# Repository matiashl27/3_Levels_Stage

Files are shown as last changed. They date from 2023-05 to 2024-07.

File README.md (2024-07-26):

# Strobe-enhanced microscopy stage for microfluidic droplet generation 

The strobe-enhanced microscopy stage is a free and open-source workstation for imaging fast processes, particularly developed for microfluidic droplet generation. It uses the lens from the Raspberry Pi Camera to produce a microscope with a field of view of almost 1mm and a strobe illumination based on a high-power LED for imaging fast-moving objects. Custom electronics allow the synchronization between the LED and the camera to capture sharp images of fast-moving droplets and other objects.

> **Note:** Most parts of this stage are original designs, and some items were modified from the open-source hardware [OpenFlexure flat-top microscope](https://rwb27.gitlab.io/openflexure-flat-top-microscope/), this includes some elements on this page and in the assembly instructions.

Find about more about this platform and other open-source hardware for bioimaging on the [LIBRE hub website](https://librehub.github.io/). Follow us! [#twitter](https://twitter.com/WenzelLab) [#YouTube](https://www.youtube.com/@librehub) [#LinkedIn](https://www.linkedin.com/company/92802424) [#instagram](https://www.instagram.com/wenzellab/) [#Printables](https://www.printables.com/@WenzelLab), [IIBM website](https://ingenieriabiologicaymedica.uc.cl/en/people/faculty/821-tobias-wenzel)

<!--- ## Table of Contents --->

<!--- ## Background --->

## Usage

### Instructions

* [Assembly instructions](https://wenzel-lab.github.io/strobe-enhanced-microscopy-stage/)
    * [Parts list](https://wenzel-lab.github.io/strobe-enhanced-microscopy-stage/3-level-station_BOM.html)
    * [Software installation](https://wenzel-lab.github.io/strobe-enhanced-microscopy-stage/software-installation.html)
* Usage instructions
	* [Software usage](https://wenzel-lab.github.io/strobe-enhanced-microscopy-stage/usage.html)

This project is documented with GitBuilding - an OpenSource project for documenting hardware projects. For more information on the GitBuilding project, or how
to install GitBuilding please see the [GitBuilding website](http://gitbuilding.io)

## Design files and source code

* Hardware designs
    * [Microscope hardware and assembly instructions (source)](https://github.com/wenzel-lab/strobe-enhanced-microscopy-stage)
    * [Pi Hat](https://github.com/wenzel-lab/moldular-microfluidics-workstation-controller/tree/master/module-pi/pi_pcb)
    * [Strobe module](https://github.com/wenzel-lab/moldular-microfluidics-workstation-controller/tree/master/module-fast-imaging)
* Software source code
    * [Microscope server](https://github.com/wenzel-lab/moldular-microfluidics-workstation-controller/blob/master/module-pi/webapp.zip) (This code runs on the built-in Raspberry Pi and includes the web application for the user interface.)
    * Microscope operating system (This collates all software and builds a pre-written SD card image for the Raspberry Pi.) - Coming soon
 
### How do I edit the documentation?

To edit the documentation you do not need to install anything, but you will need to
install something to build the final version of the documentation (such as a website).
The documentation files can be opened in a plain text editor such as Windows Notepad,
Notepad++, gedit, VS Code, etc. GitBuilding also comes with a browser-based editor that
displays has a live display of the final HTML documentation.

If you have ever used [markdown](https://www.markdownguide.org/basic-syntax/) you will
notice that the files you are editing are markdown files. GitBuilding uses an extended
markdown syntax (that we call BuildUp). This allows you to keep track of parts in the
documentation. More detail on the documentation is available on the
[GitBuilding website](https://gitbuilding.io/syntax/). There is also additional
[syntax for configuration](https://gitbuilding.io/syntax/buildconfsyntax), and for
[part libraries](https://gitbuilding.io/syntax/builduplibrary/).

## Contribute

You're free to fork the project and enhance it. If you have any suggestions to improve it or add any additional functions make a pull-request or [open an issue](https://github.com/wenzel-lab/strobe-enhanced-microscopy-stage/issues/new).
For interactions in our team and with the community applies the [GOSH Code of Conduct](https://openhardware.science/gosh-2017/gosh-code-of-conduct/).

## License

[CERN OHL 2W](LICENSE) © Pierre Padilla-Huamantinco, Matías Hurtado, and Tobias Wenzel. This project is Open Source Hardware - please acknowledge us when using the hardware or sharing modifications.

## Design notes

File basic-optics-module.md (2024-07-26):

# Assemble the basic optics module

{{BOM}}

[M3 nut]: parts/mech/nuts.md "{cat:mechanic}"
[M2x5mm cap head screw]: parts/mech/M2-5.md "{cat:mechanic}"
[M3x10mm cap head screw]: parts/mech/M3-10.md "{cat:mechanic}"
[Raspberry Pi Camera Module v2]: parts/elect/rpi-camera-v2.md "{cat:electronic}"
[Pi camera ribbon cable]: parts/elect/rpi-camera-ribbon-cable.md "{cat:electronic}"
[1.5mm Ball-end Allen key]: parts/tools/1.5mmBallEndAllenKey.md "{cat:tool}"
[Pi Camera lens tool]: parts/tools/pi_camera_lens_tool.md "{cat:tool, note: 'This should come with the Raspberry Pi Camera Module. If it is missing, you can 3D print a workaround lens remover.'}"
[Lens spacer]: models/lens-spacer.stl "{previewpage}"
[Pi Camera platform]: models/camera-platform.stl "{previewpage}"
[Nitrile gloves]: parts/consumables/gloves.md "{cat:consumable}"

The imaging optics for this workstation version consist of the Raspberry Pi camera and the lens from the camera. To create a microscope, the lens is separated from the camera. This makes quite a good microscope objective with a field of view about 950μm across.

## Visually inspect the lens spacer {pagestep}

Take the [lens spacer][Lens spacer](fromstep){qty:1, cat:printedpart} and confirm that:

* It has been printed in black.
* It is dust free (You can blow air through to clean it)
* The central shaft is not obstructed by strings of plastic.

## Remove Pi Camera Lens {pagestep}

>! **Caution!** The camera board is static sensitive. Before touching the Pi Camera, touch a metal-earthed object. If you own one, consider wearing an anti-static strap.

* Use [nitrile gloves][Nitrile gloves]{Qty:2} to manipulate camera and lens. 
* Take the [Pi Camera][Raspberry Pi Camera Module v2]{qty:1} out of the package. Make sure to **hold it only by the sides of the board**.
* Take the protective film off the lens.
* Take the [Pi Camera lens tool]{qty: 1} and place it over the lens
* Slowly unscrew the lens (About 4 full turns of the tool)
* Carefully lift off the lens.
* Save the lens and the camera.

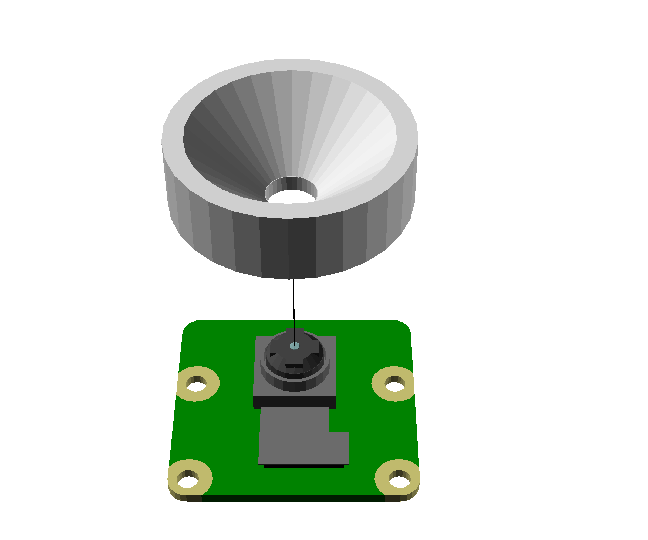
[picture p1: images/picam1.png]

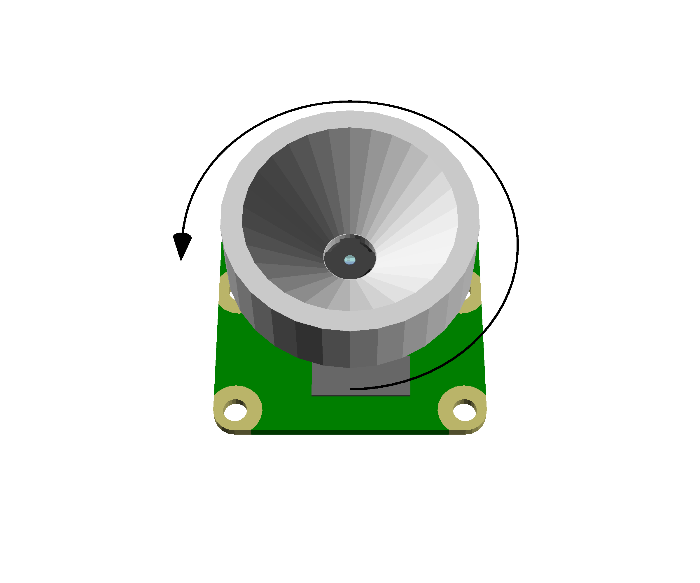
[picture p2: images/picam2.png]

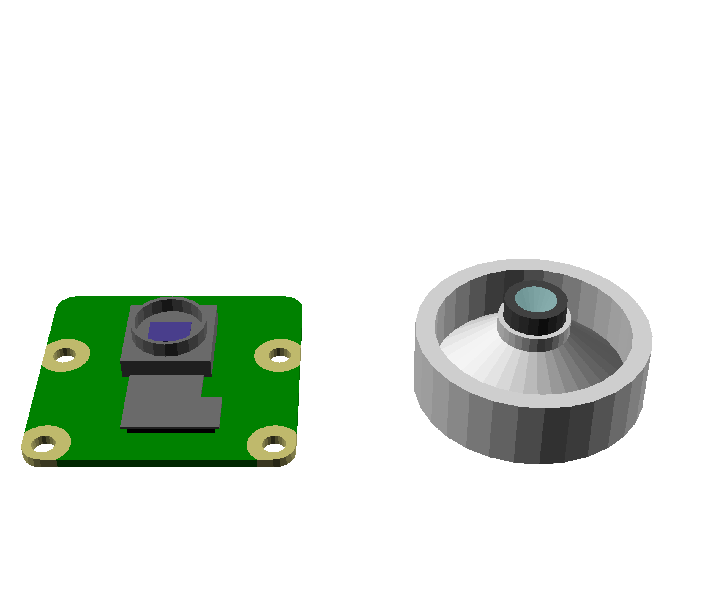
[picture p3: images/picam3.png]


## Push-fit the lens {pagestep}

* Place the Pi Camera lens on a clean surface with the side opposite the camera sensor on the bottom.
* Push the lens spacer down onto the lens until it clicks into place.

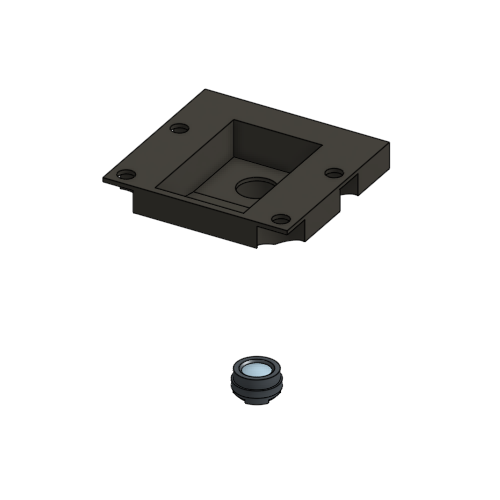
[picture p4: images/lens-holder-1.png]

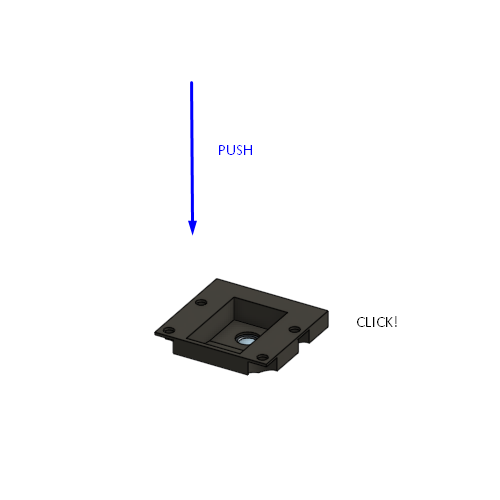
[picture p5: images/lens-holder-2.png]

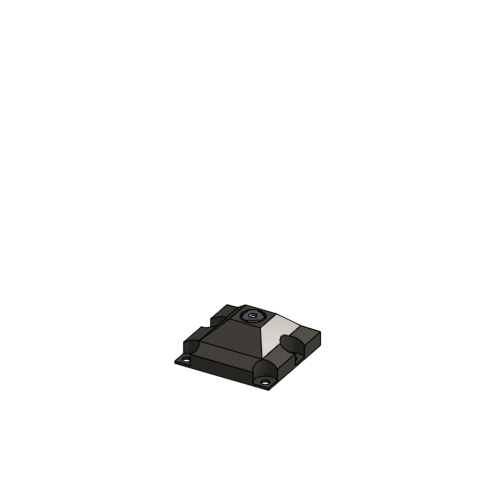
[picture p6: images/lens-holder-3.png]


## Attach the Pi Camera {pagestep}

* Take the Pi Camera and place it on top of the [pi camera platform][Pi Camera platform](fromstep){qty:1, cat:printedpart}.
* Place the lens spacer over the camera.
* Use four [M2x5mm cap head screws][M2x5mm cap head screw]{qty:4} to secure the three parts together using a [1.5mm Ball-end Allen key]{qty:1}

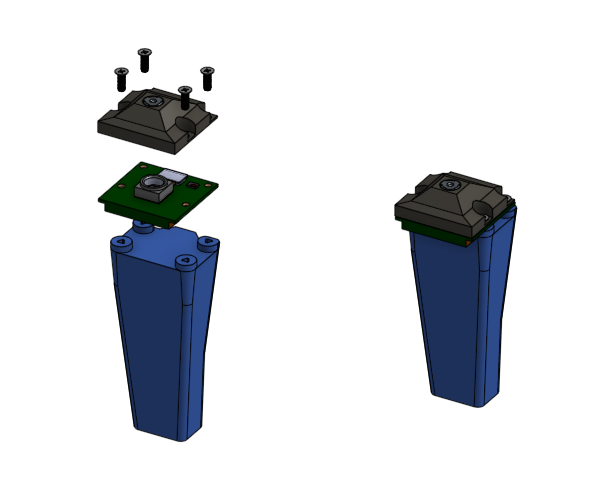
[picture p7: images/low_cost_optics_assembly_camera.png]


## Attach the mounting screw {pagestep}

* Take an [M3 nut]{qty:1} and push it into the nut trap from the top
* Take an [M3x10mm cap head screw]{qty: 1} and screw it into the nut.
* Only screw it in a couple of turns. About 5 mm of thread should still be visible.

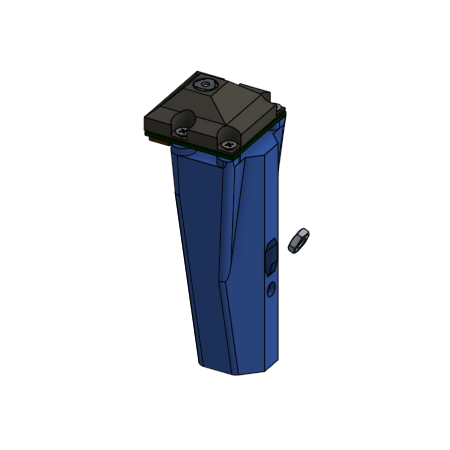
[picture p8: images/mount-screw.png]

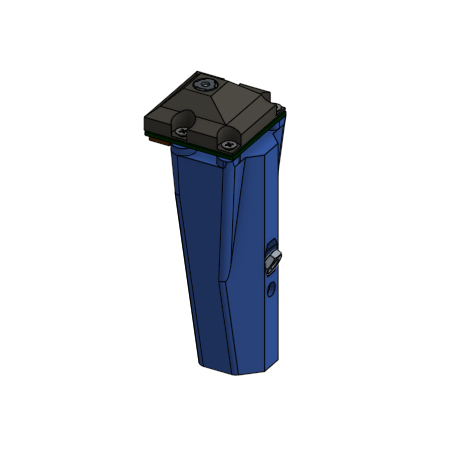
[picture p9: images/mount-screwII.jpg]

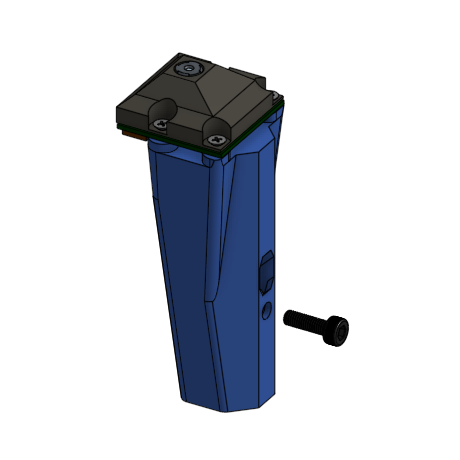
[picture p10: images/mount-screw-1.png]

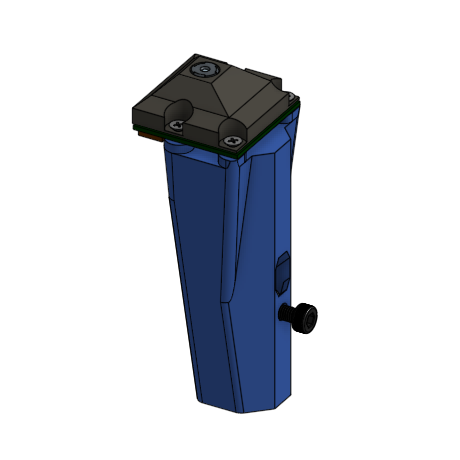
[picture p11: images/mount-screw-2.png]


## Connect ribbon cable {pagestep}

* Take the [Pi Camera ribbon cable][Pi camera ribbon cable]{qty:1}
* Pull the catch forward on the exposed Pi Camera connector
* Insert the ribbon cable with the contacts towards the board
* Close the catch on the connector

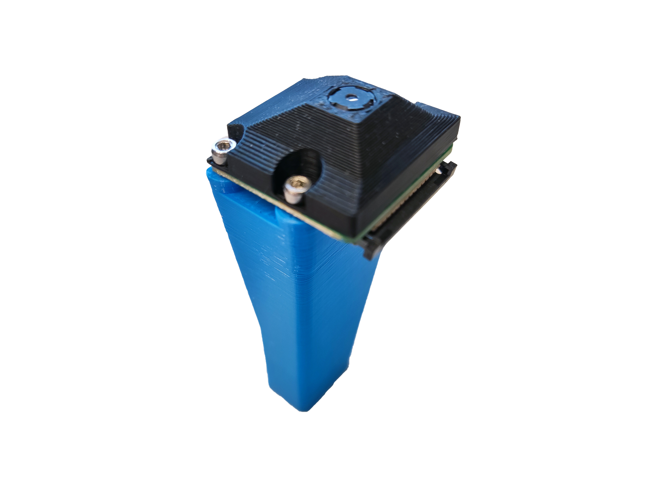
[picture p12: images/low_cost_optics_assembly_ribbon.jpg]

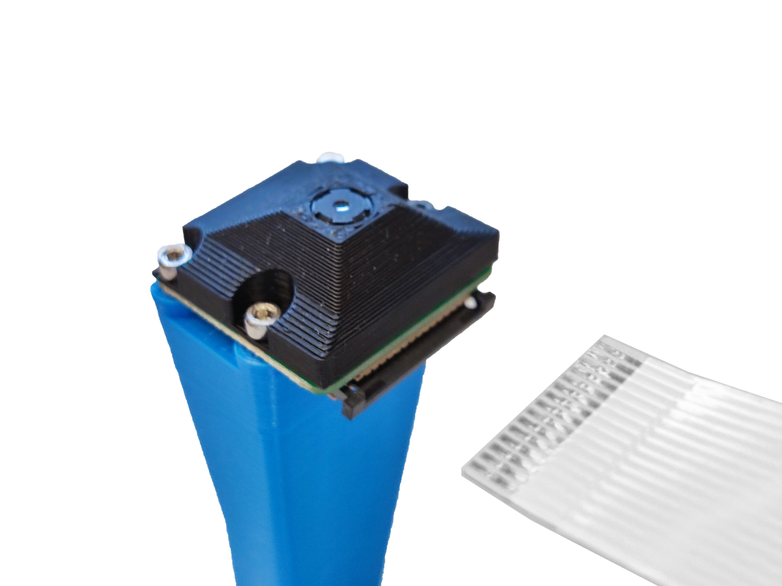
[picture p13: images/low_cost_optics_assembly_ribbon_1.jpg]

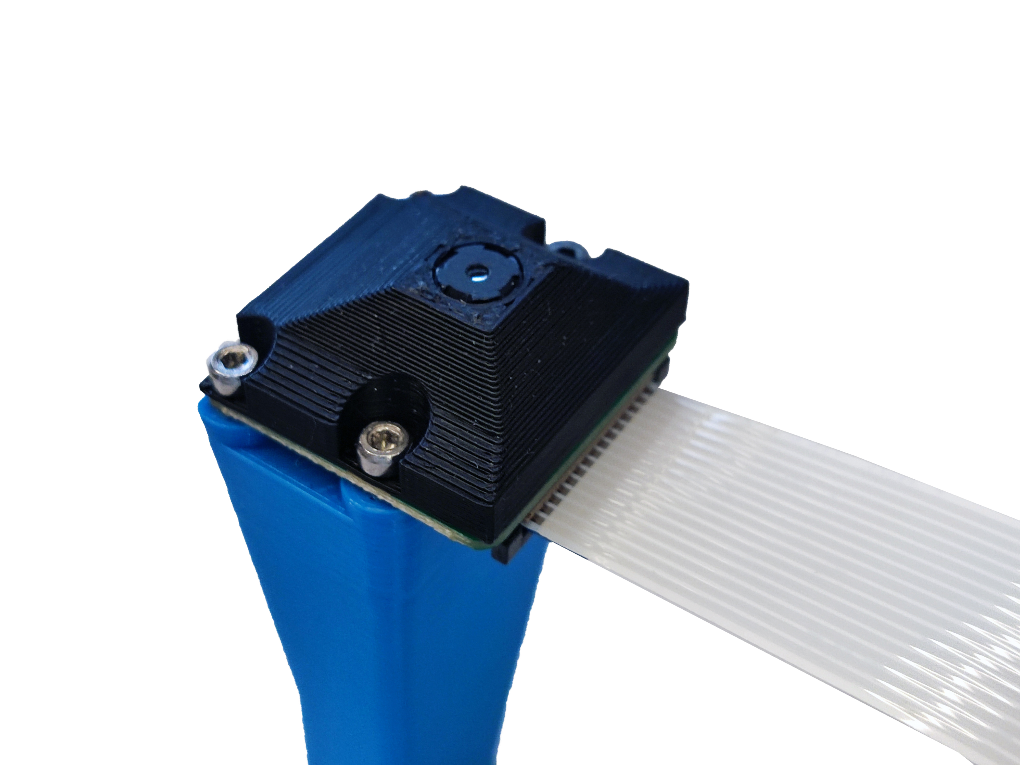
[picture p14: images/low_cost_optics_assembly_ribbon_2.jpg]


## Set the complete module aside {pagestep}

Set the [complete optics module]{output, qty:1} aside in a safe place.

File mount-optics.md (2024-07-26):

# Mount the optics

{{BOM}}

[2.5mm Ball-end Allen key]: parts/tools/2.5mmBallEndAllenKey.md "{cat:tool}"

## Mount the optics assembly {pagestep}

* Get the [2.5mm Ball-end Allen key]{qty:1} ready
* Take the [complete optics module](fromstep){qty:1, cat:subassembly} and pass it between the top and middle plates of the [main structure](fromstep){qty:1, cat:subassembly}.
* Insert the exposed mounting screw on the optics module through the keyhole on the z-actuator.

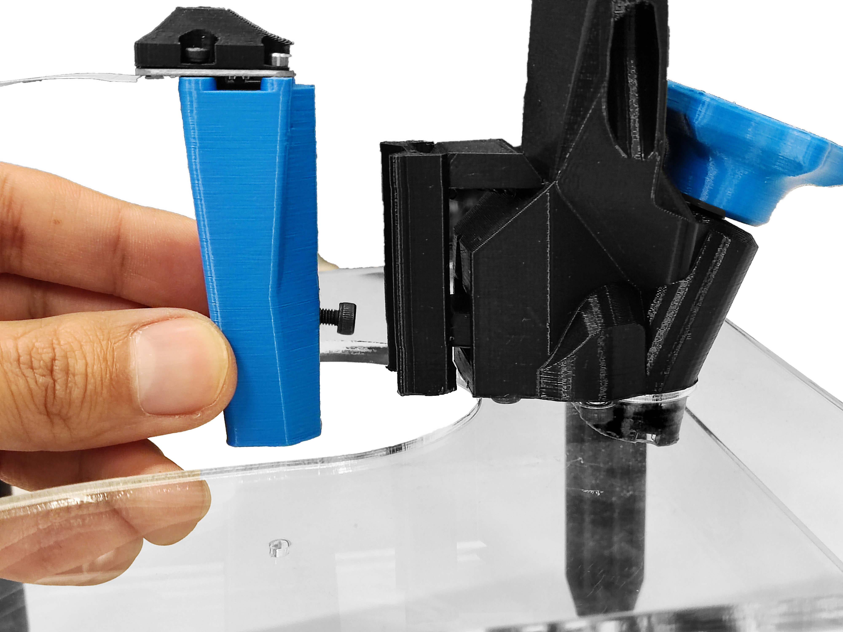
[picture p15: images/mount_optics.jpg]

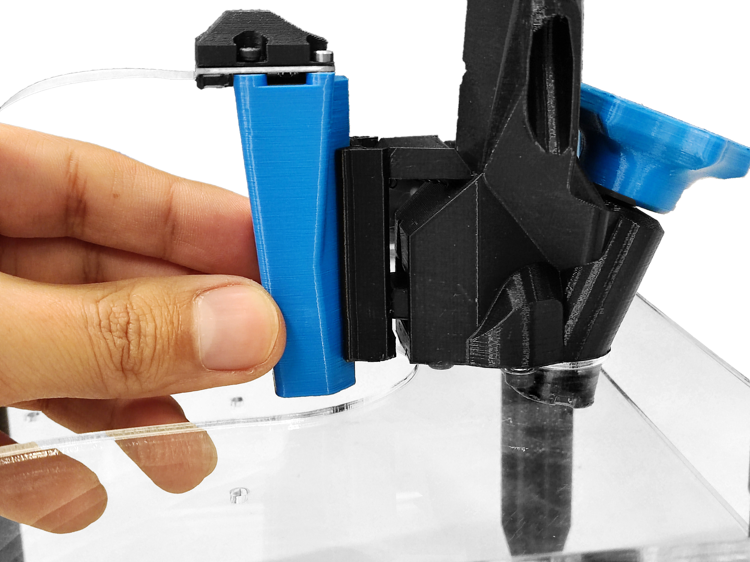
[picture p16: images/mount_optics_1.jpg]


## Adjust the optics assembly {pagestep}

* Insert the Allen key through the teardrop-shaped hole on the front of the z-actuator until it engages with the mounting screw.
* Slide the optics module up the keyhole.
* Tighten the screw with the Allen key to lock the optics.
* The optics module position can be changed later using the thumbwheel or mounting screw for different applications. 



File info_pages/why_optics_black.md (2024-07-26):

# Why print the optics module or lens spacer in black?

The optics module or lens spacer is used to separate the imaging optics from the camera sensor. In an ideal microscope the only light that reaches the camera sensor should be the light focused by these optics. 

We can limit reflected light using black filament. This will absorb more of the stray light. Black filament is also more opaque than other filaments. This means that less light will be transmitted through the walls of the optics module.

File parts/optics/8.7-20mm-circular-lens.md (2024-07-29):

# 8.7° 20mm Circular Beam Optics

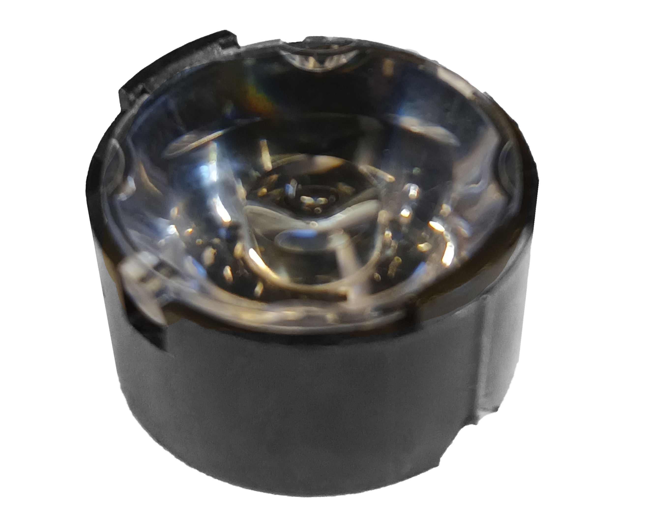
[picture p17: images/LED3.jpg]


_Suppliers:_ 

* [Luxeonstar / Lens](https://luxeonstar.com/product/10193/)

* [Luxeonstar / Holder](https://luxeonstar.com/product/10235/)

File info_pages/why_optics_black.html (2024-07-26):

# Strobe-enhanced microscopy stage

by Pierre Padilla-Huamantinco, Matías Hurtado-Labarca, and Tobias Wenzel

Latin American Hub for Bioimaging Through Open Hardware (LIBRE hub)

# Why print the optics module or lens spacer in black?

The optics module or lens spacer is used to separate the imaging optics from the camera sensor. In an ideal microscope the only light that reaches the camera sensor should be the light focused by these optics.

We can limit reflected light using black filament. This will absorb more of the stray light. Black filament is also more opaque than other filaments. This means that less light will be transmitted through the walls of the optics module.

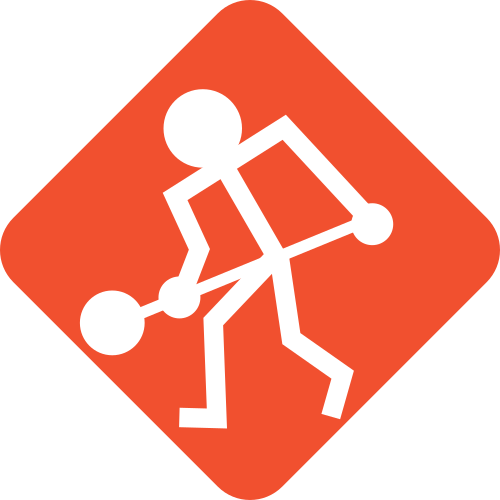
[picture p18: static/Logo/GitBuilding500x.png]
GitBuilding logo
 Documentation powered by GitBuilding (https://gitbuilding.io)

©2024 Pierre Padilla-Huamantinco, Matías Hurtado-Labarca, and Tobias Wenzel

Contact: librehub@uc.cl

Strobe-enhanced microscopy stage is released under CERN-OHL-S-2.0.

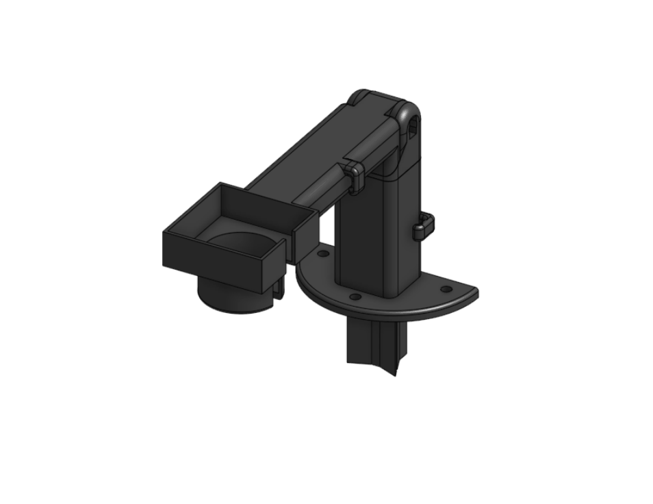
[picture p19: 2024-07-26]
variants/images/3d-custom-cover.gif

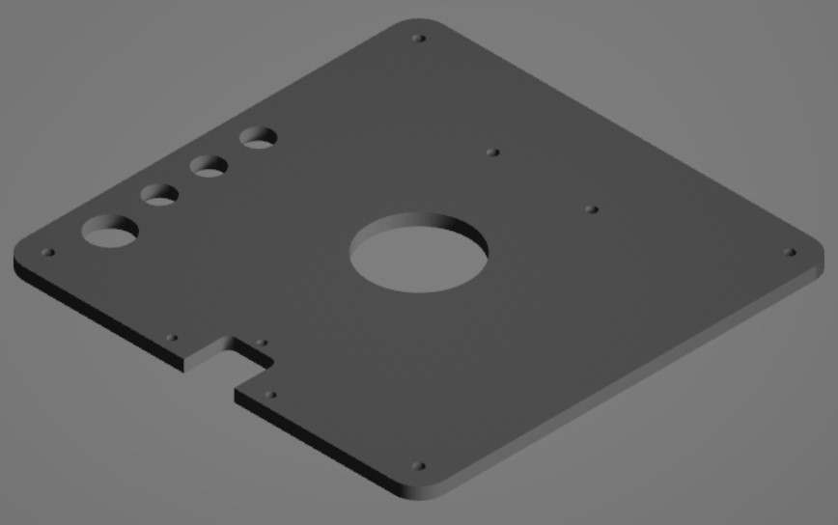
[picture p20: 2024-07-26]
variants/images/custom-top-plate.jpg

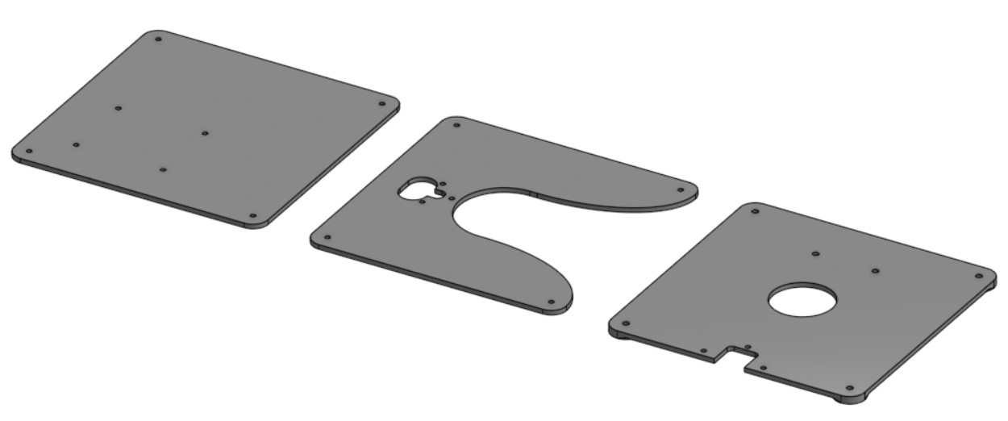
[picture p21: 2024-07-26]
variants/images/plates3d.jpg

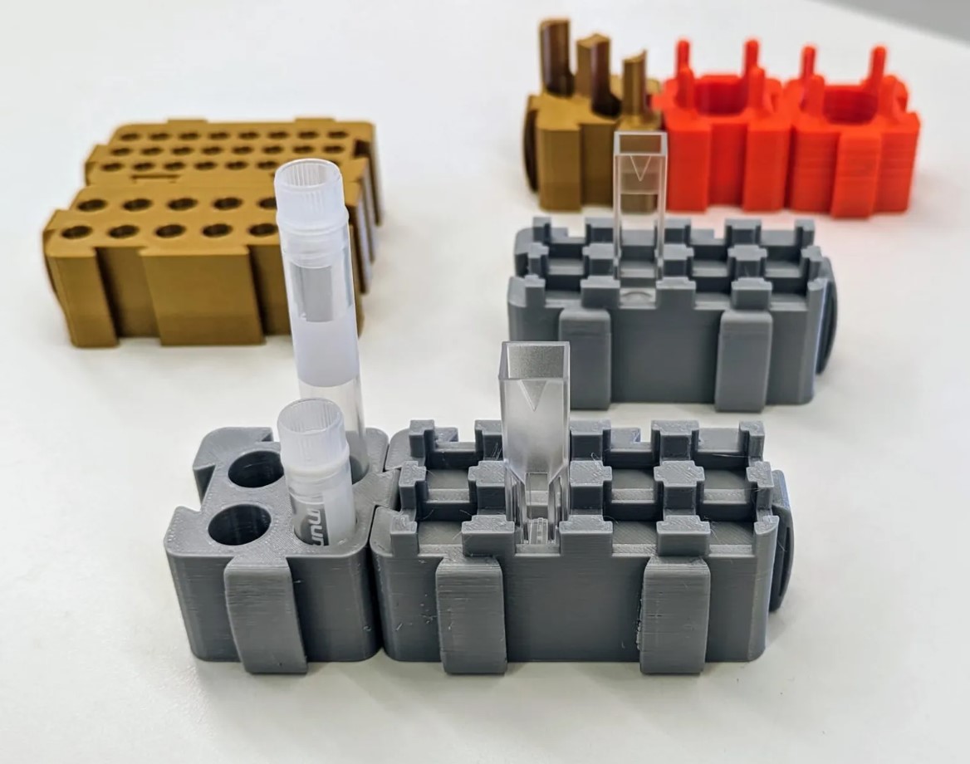
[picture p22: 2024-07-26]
variants/images/3d-tube-holders.jpg

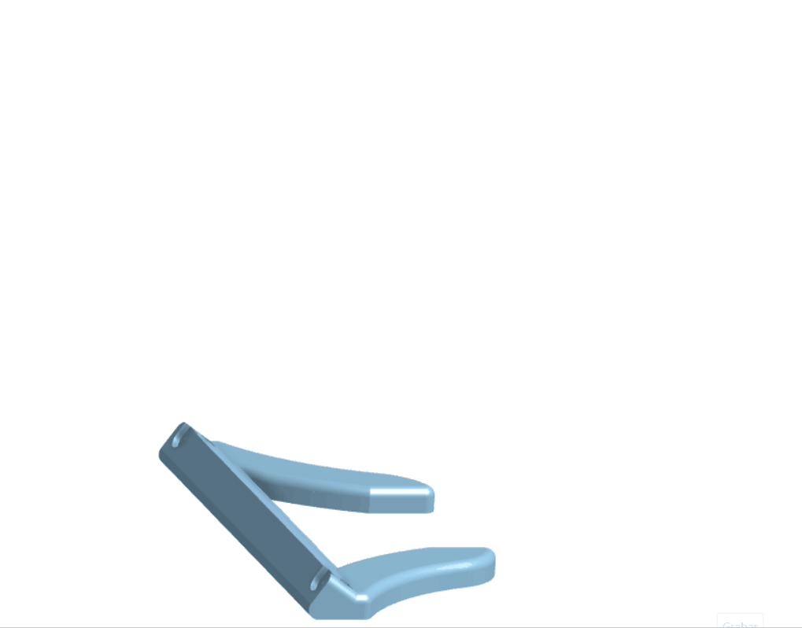
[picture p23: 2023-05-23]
variants/images/3d-screen-frame.gif

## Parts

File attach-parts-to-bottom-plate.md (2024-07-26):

# Attach parts to the bottom plate

{{BOM}}

[M3x15mm cap head screw]: parts/mech/M3-15.md "{cat:mechanic}"
[M3 nut]: parts/mech/nuts.md "{cat:mechanic}"
[2.5mm Ball-end Allen key]: parts/tools/2.5mmBallEndAllenKey.md "{cat:tool}"
[Bottom plate]: parts/materials/bottom-plate.md "{cat:lasercutpart}"
[Standoff-S]: models/standoff-S.stl "{previewpage}"
[Foot-M]: models/foot-M.stl "{previewpage}"
[Nut tool]: models/actuator-assembly-tools.stl "{previewpage}"

## Prepare the small standoffs {pagestep}

* Take an [M3 nut]{qty:4} and push it into the nut trap from the small [standoff][Standoff-S]. Insert one into each of the standoffs using the [nut insertion tool][Nut tool](fromstep){qty:1, cat:printedtool}.

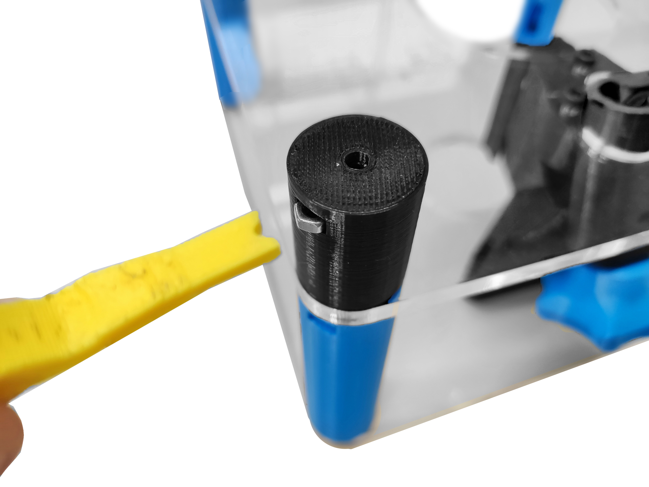
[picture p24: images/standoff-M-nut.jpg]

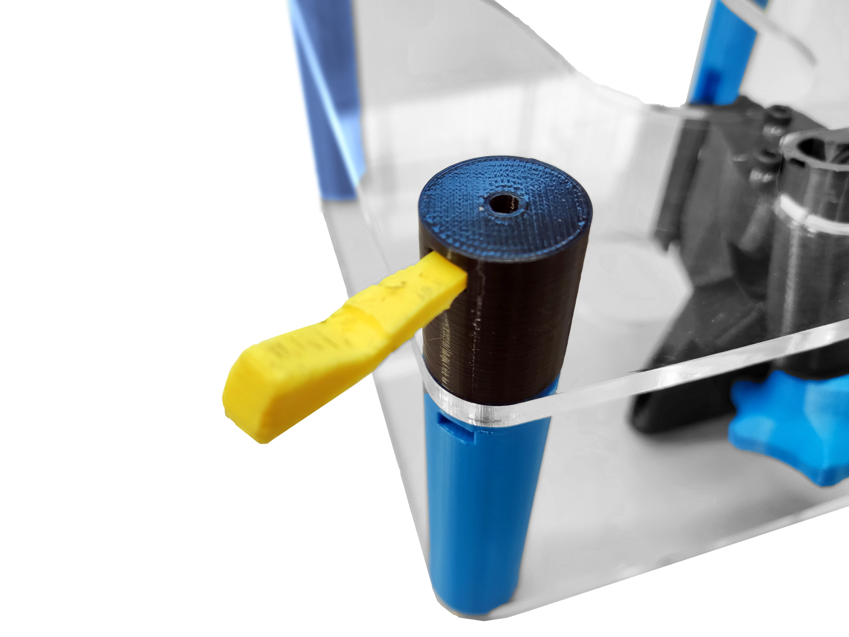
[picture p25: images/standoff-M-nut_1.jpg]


## Prepare the feet {pagestep}

* Insert a [M3x15mm cap head screw]{qty: 4} into each [foot][Foot-M](fromstep){qty: 4, cat:printedpart} using the large hole that comes out the side of the [foot][Foot-M]. The screw should poke out the end of the part as shown.
* Use a [2.5mm ball-ended hex key][2.5mm Ball-end Allen key]{qty:1} to turn the screw.

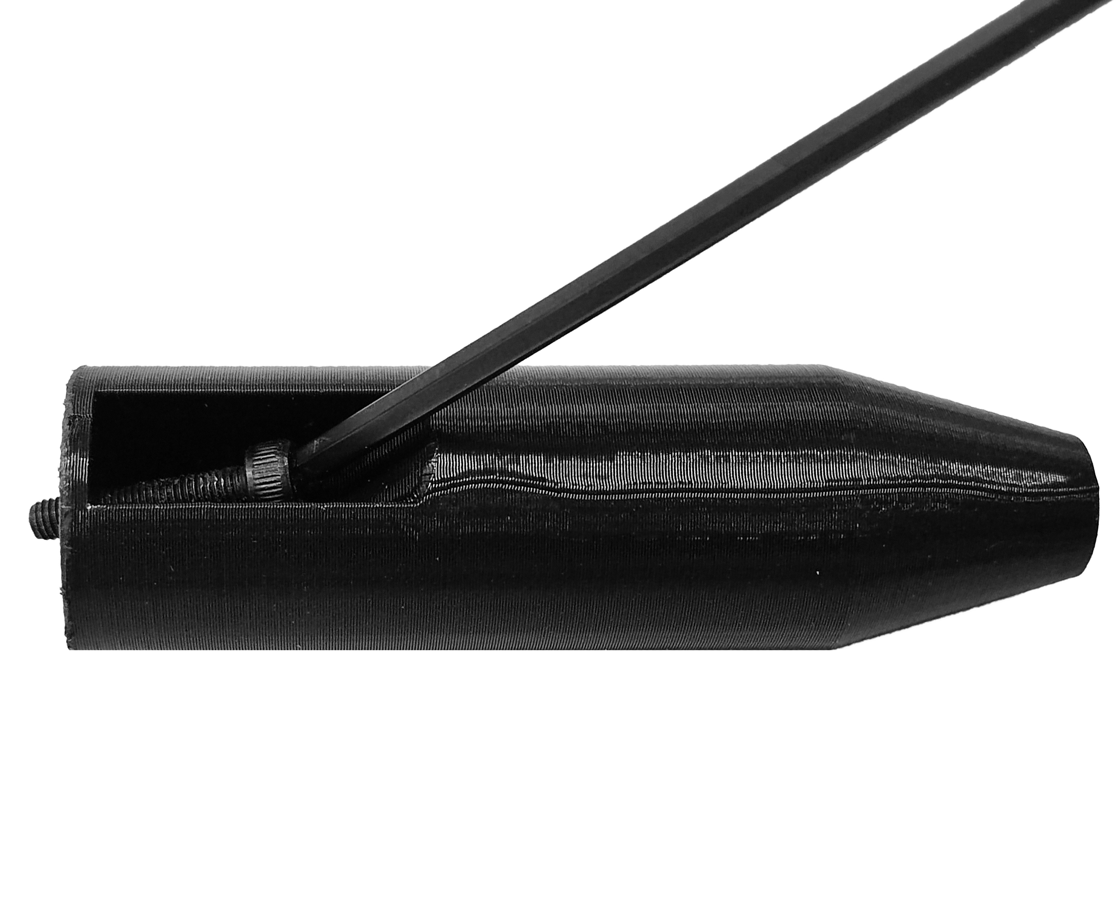
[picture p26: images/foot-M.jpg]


## Attach the bottom plate and the foot {pagestep}

* Place the bottom plate above the small standoffs. The four holes for attaching the Raspberry Pi should be on the opposite side of the focusing mechanism, as shown.
* Attach each [foot][Foot-M] to one of the corners of the [bottom plate][Bottom plate](fromstep){qty:1}.
* Use the [nut insertion tool][Nut tool] and the [2.5mm ball-ended hex key][2.5mm Ball-end Allen key] to secure the three parts together.
* Nut traps should be accessible for future calibrations and upgrades.

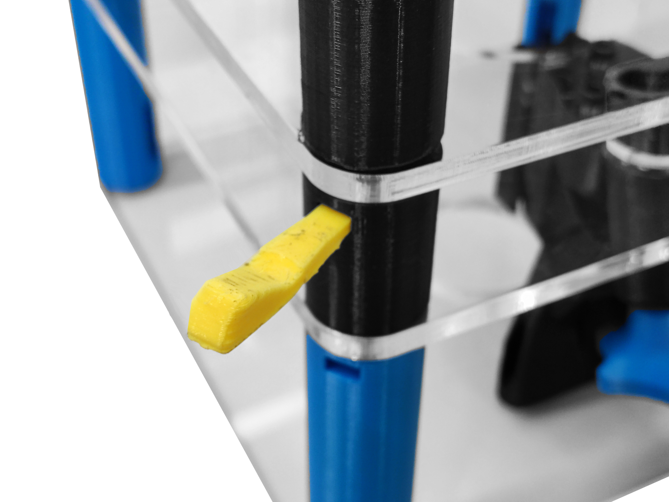
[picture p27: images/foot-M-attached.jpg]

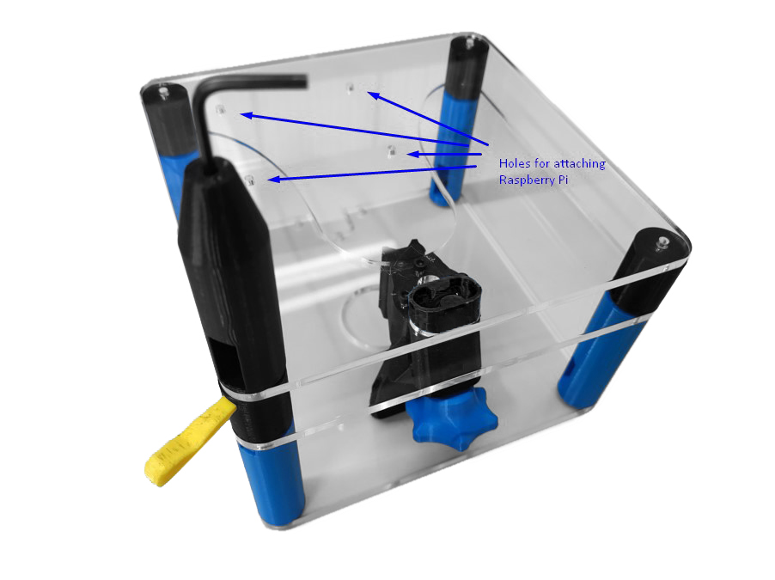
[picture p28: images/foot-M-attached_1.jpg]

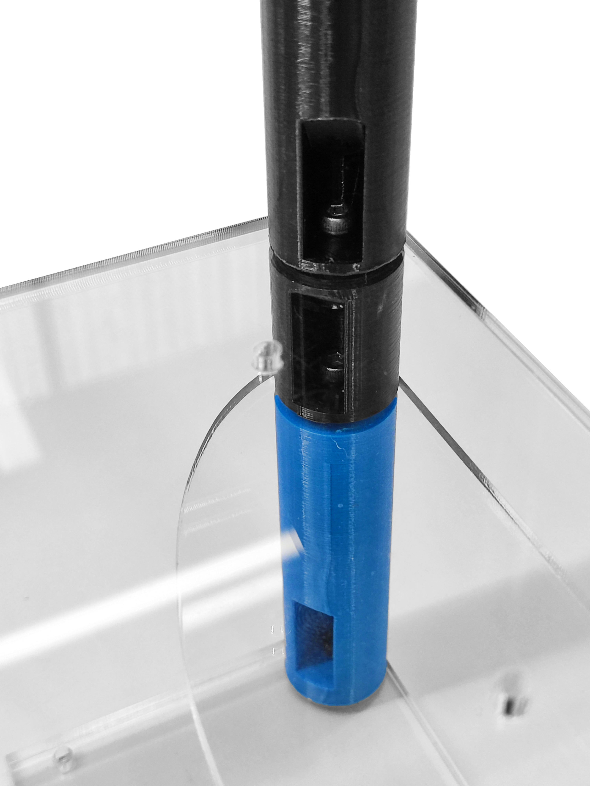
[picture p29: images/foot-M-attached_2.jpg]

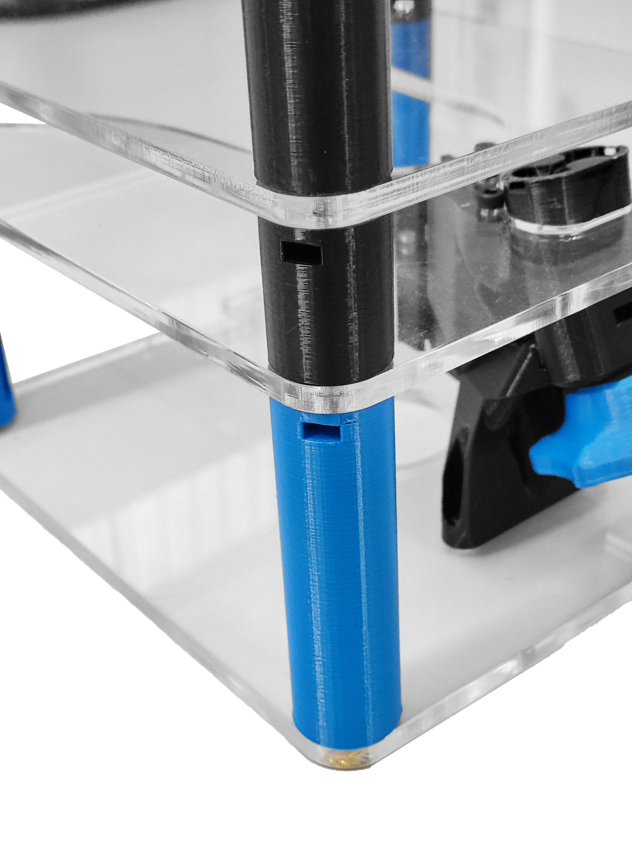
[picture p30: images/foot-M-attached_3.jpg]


At this point, the [main structure]{output,qty:1} is complete.

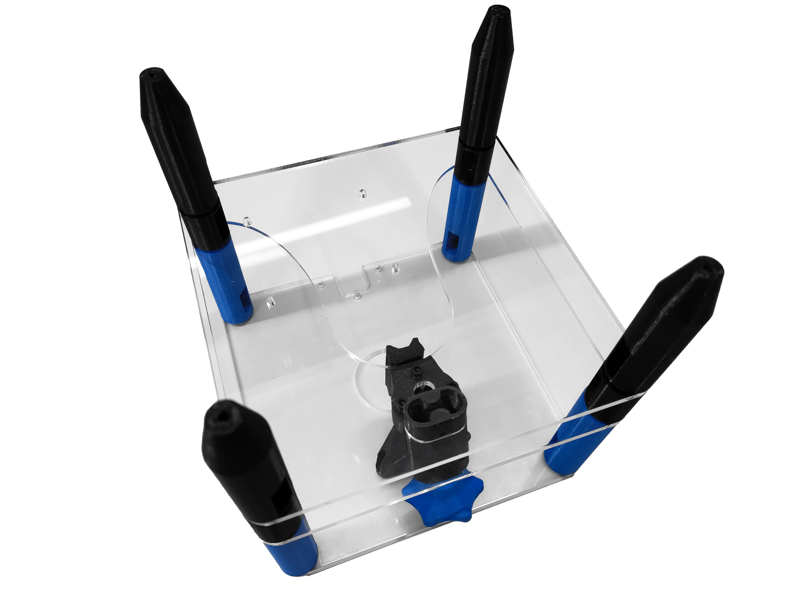
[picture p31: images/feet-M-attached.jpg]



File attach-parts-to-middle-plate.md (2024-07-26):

# Attach parts to the middle plate

{{BOM}}

[M3x10mm cap head screw]: parts/mech/M3-10.md "{cat:mechanic}"
[M3x15mm cap head screw]: parts/mech/M3-15.md "{cat:mechanic}"
[M3 nut]: parts/mech/nuts.md "{cat:mechanic}"
[Middle plate]: parts/materials/middle-plate.md "{cat:lasercutpart}"
[2.5mm Ball-end Allen key]: parts/tools/2.5mmBallEndAllenKey.md "{cat:tool}"
[Nut tool]: models/actuator-assembly-tools.stl "{previewpage}"
[Standoff-S]: models/standoff-S.stl "{previewpage}"
[Standoff-M]: models/standoff-M.stl "{previewpage}"

You will also need the parts you assembled in previous sections.

## Screw into the focusing assembly {pagestep}

* Attach the [middle plate][Middle plate](fromstep){qty:1} to the [focusing mechanism](fromstep) using three [M3x10mm cap head screws][M3x10mm cap head screw]{qty: 3}.
* Use a [2.5mm ball-ended hex key][2.5mm Ball-end Allen key]{qty:1} to turn the screws.




## Attach the small standoffs {pagestep}

* Insert a [M3 nut] into the nut trap of the [standoff][Standoff-M] (using the [nut insertion tool][Nut tool](fromstep){qty:1, cat:printedtool}). Do the same for the four standoffs.




* Insert a [M3x15mm cap head screw]{qty: 4} into each small [standoff][Standoff-S](fromstep){qty: 4, cat:printedpart} using the large hole that comes out the side of the [standoff][Standoff-S]. The screw should poke out the end of the part as shown.
* Use a [2.5mm ball-ended hex key][2.5mm Ball-end Allen key]{qty:1} to turn the screw.



* Attach each small [standoff][Standoff-S] to one of the corners of the [middle plate][Middle plate].
* Use the [nut insertion tool][Nut tool] and the [2.5mm ball-ended hex key][2.5mm Ball-end Allen key] to secure the other three parts.





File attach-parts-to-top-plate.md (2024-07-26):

# Attach parts to the top plate

{{BOM}}

[Heat insert]: parts/mech/Hinsert.md "{cat:mechanic}"
[M3x8mm cap head screw]: parts/mech/M3-8.md "{cat:mechanic}"
[M3x10mm cap head screw]: parts/mech/M3-10.md "{cat:mechanic}" 
[Top plate]: parts/materials/top-plate.md "{cat:lasercutpart}"
[Soldering iron]: parts/tools/soldiron.md "{cat:tool}"
[2.5mm Ball-end Allen key]: parts/tools/2.5mmBallEndAllenKey.md "{cat:tool}"
[Focusing assembly]: models/focusing-assembly.stl "{previewpage}"
[Standoff-M]: models/standoff-M.stl "{previewpage}"

You will also need the parts you assembled in previous sections.

## Prepare the top plate {pagestep}

* Positionate a [heat insert][Heat insert]{qty:4} in each corner of the [top plate][Top plate](fromstep){qty:1}.
* Apply heat to each [insert][Heat insert] (using a [soldering iron]{qty:1}) and use gentle force to push it into position, as described in the [guide to use heat-set inserts].
* Repeat this step to put two more [inserts][Heat insert]{qty:2} in the plate to attach the focusing assembly.






## Prepare the standoffs {pagestep}

* Insert a [M3x10mm cap head screw]{qty: 4} into each [standoff][Standoff-M](fromstep){qty: 4, cat:printedpart} using the large hole that comes out the side of [them][Standoff-M]. The screw should poke out the end of the part as shown.
* Use a [2.5mm ball-ended hex key][2.5mm Ball-end Allen key]{qty:1} to turn the screw.




## Attach the standoffs {pagestep}

* Attach each [standoff][Standoff-M] to one of the corners of the [top plate][Top plate].




## Attach the focusing assembly {pagestep}

* Use a [M3x8mm cap head screw]{qty: 2} on either side of the [focusing mechanism](fromstep){qty:1, cat:subassembly}, attach it to the top plate.





[guide to use heat-set inserts]: https://hackaday.com/2019/02/28/threading-3d-printed-parts-how-to-use-heat-set-inserts/

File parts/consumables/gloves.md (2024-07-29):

# Nitrile gloves



They safeguard sensitive electronic components from contamination, oils, and static discharge.

These gloves prevent potential damage during assembly, repair, or handling of electronic devices.

*Supplier:* [bioquimica.cl](https://www.bioquimica.cl/guantes-de-nitrilo-sin-polvo-caja-100-un)

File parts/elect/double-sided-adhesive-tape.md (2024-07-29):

# Double-sided Adhesive Tape

Adhesive coatings on both sides for joining surfaces.
It's widely used in bonding applications, eliminating the need for visible fasteners.
This tape is commonly utilized in crafting, construction, and packaging for discreet and secure adhesion.



_Supplier:_ [Luxeonstar](https://www.luxeonstar.com/mounting-tape-for-carclo-20mm-round-optic-holders)

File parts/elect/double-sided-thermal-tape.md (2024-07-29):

# Double-sided Thermal Tape

Tape with adhesive on both sides, specifically designed for transferring heat between two surfaces.
It is commonly used to attach heat sinks or cooling components to electronic devices for effective heat dissipation.
This tape ensures efficient thermal management in applications such as electronics, computers, and LED lighting.



_Supplier:_ [Luxeonstar](https://luxeonstar.com/product/lxt-s-12/)

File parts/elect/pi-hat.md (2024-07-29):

# Pi Hat
Expansion board designed to fit onto a Raspberry Pi's GPIO pins.
It provides additional functionalities, such as sensors, interfaces, and integrated circuits, to enhance the capabilities of the Raspberry Pi.
HATs are plug-and-play modules, making them easy to use and customize for various projects.





*This is a custom open-source board documented* [here](https://github.com/wenzel-lab/modular-microfluidics-workstation-controller/tree/master/module-pi)

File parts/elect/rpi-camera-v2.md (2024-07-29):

# Raspberry Pi camera V2

Official camera module designed for Raspberry Pi boards.
It features a high-quality image sensor and a lens with adjustable focus.


*Supplier:* [MCI electronics](https://mcielectronics.cl/shop/product/camara-v2-para-raspberry-pi-raspberry-pi-21481/)

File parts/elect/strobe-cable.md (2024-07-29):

# Strobe Cable

*This is a custom open-source board documented* [here](https://github.com/wenzel-lab/open-microfluidics-workstation/)

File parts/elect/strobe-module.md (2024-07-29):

# Strobe Module





This is a custom open-source board documented [here](https://github.com/wenzel-lab/modular-microfluidics-workstation-controller/tree/master/module-fast-imaging)

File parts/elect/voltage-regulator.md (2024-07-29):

# Voltage Regulator
It is used to control manually exactly how much electricity circulates. 



_Supplier:_ [AFEL](https://afel.cl/producto/regulador-de-voltaje-step-down-dc-dc-lm2596-con-voltimetro/)

This regulator has modifications documented [here](https://github.com/wenzel-lab/modular-microfluidics-workstation-controller)

>! In some models, the electronics of this can be exposed, be sure to cover them to avoid possible accidents.

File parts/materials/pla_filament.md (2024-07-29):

# PLA filament

The microscope design has been tested using PLA filament only. PLA is the most common 3D printer filament. It is easy to use and has low part shrinkage. We have found that the lifetime of the microscope is affected by the quality of the PLA filament, as such we recommend buying high quality filament and storing the filament in a dry sealed container before printing.

_Supplier:_ [Esun](https://www.esun3d.com/) or [Todo Toner](https://www.todotoner.cl/impresoras/impresoras-3d/filamentos/pla-plus-1kg-negro-esun)

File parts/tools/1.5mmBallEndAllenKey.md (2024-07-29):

# 1.5 mm Ball-end Allen Key

Tool used to drive screws or bolts with hexagonal sockets. It has a metal shaft with a hexagonal cross-section. They come in different sizes for various applications.

It is important that the Allen key has a ball end:



*Supplier:* [ferretería.cl](https://ferreteria.cl/ficha/5866/juego-de-llave-allen-larga-de-bola-metrico-9-pzs-tactix)

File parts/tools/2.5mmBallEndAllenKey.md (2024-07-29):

# 2.5 mm Ball-end Allen Key

Tool used to drive screws or bolts with hexagonal sockets. It has a metal shaft with a hexagonal cross-section. They come in different sizes for various applications.

It is important that the Allen key has a ball end:



*Supplier:* [ferretería.cl](https://ferreteria.cl/ficha/5866/juego-de-llave-allen-larga-de-bola-metrico-9-pzs-tactix)

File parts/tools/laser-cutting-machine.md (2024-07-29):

# Laser cutting machine 

High-precision tool that uses a focused laser beam to cut through or engrave various materials.

It offers versatility in cutting intricate shapes, patterns, and designs in materials like wood, acrylic, metal and fabric.

Laser cutting machines are used in industries like manufacturing, crafting, signage, and engineering for precise and efficient material processing.



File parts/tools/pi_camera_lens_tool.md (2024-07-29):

# Pi camera lens tool

This should come with the [Raspberry Pi Camera Module](http://localhost:6178/live/editor1/parts/elect/rpi-camera-v2.html). If it is missing, you can 3D print a workaround lens remover.



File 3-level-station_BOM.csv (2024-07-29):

Name in documentation | Category | Qty | Full Name | Notes
#1 pozidrive screwdriver | tool | 1
1.5mm Ball-end Allen key | tool | 1
2 pin Du Pont connector female housing | electronic | 1
2.5mm Ball-end Allen key | tool | 1
30x30x10mm Heat sink | electronic | 1
52x18x0.5cm Acrylic sheet | material | 1
Black PLA filament | material | 50 g
Conductor Flexible Cables | electronic | 2
Crimper | tool | 1
Double-sided self adhesive tape | electronic | 1
Double-sided thermal tape | electronic | 1
Heat insert | mechanic | 7 | Heat inserts
High-power star LED | electronic | 1
Laser cutting machine | tool | 1
light oil | consumable | 1 drop |  | Optional
M2x5mm cap head screw | mechanic | 4 | Screw
M3 nut | mechanic | 14
M3 washers | mechanic | 2 | Screw washer
M3x10mm cap head screw | mechanic | 11 | Screw
M3x15mm cap head screw | mechanic | 8 | Screw
M3x20mm pozi pan head screw | mechanic | 1 | M3 X Screw
M3x25mm cap head screw | mechanic | 4 | Screw
M3x25mm hex head screw | mechanic | 1 | M3 HEX screw
M3x8mm cap head screw | mechanic | 2 | Screw
Male Crimp Pin | electronic | 2
Needle-nose plier | tool | 1
Nitrile gloves | consumable | 2
O-ring | mechanic | 1
Pi Camera lens tool | tool | 1 |  | This should come with the Raspberry Pi Camera Module. If it is missing, you can 3D print a workaround lens remover.
Pi camera ribbon cable | electronic | 1
Pi HAT | electronic | 1 |  | This is a custom open-source board documented [here](https://github.com/wenzel-lab/modular-microfluidics-workstation-controller/tree/master/module-pi)
PLA filament | material | 205 g |  | Of any color you want
Precision wire cutter | tool | 1
Raspberry Pi | electronic | 1
Raspberry Pi Camera Module v2 | electronic | 1
Raspberry Pi Power Supply | electronic | 1
RepRap-style printer | tool | 1
Soldering iron | tool | 1
Star-LED lens | optical | 1
Strobe Cable | electronic | 1 |  | This is a custom connector documented [here](https://github.com/wenzel-lab/open-microfluidics-workstation/)
Strobe Module | electronic | 1 |  | This is a custom open-source board documented [here](https://github.com/wenzel-lab/modular-microfluidics-workstation-controller/tree/master/module-fast-imaging)
Strobe Power Supply | electronic | 1 | Strobe Power Supply
Utility knife | tool | 1 |  | Not a scalpel!
Voltage regulator | electronic | 1 |  | This regulator has modifications documented [here](https://github.com/wenzel-lab/open-microfluidics-workstation/)

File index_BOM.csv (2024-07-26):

Name in documentation | Category | Qty | Full Name | Notes
7-inch capacitive touch screen for Raspberry Pi | part | 1
actuator foot | printedpart | 1
base of the light holder | printedpart | 1
base piece | printedpart | 1
camera holder | printedpart | 1
cap of the light holder | printedpart | 1
focusing regulator | printedpart | 1
gripper | printedtool | 1
heat inserts | part | 6 | Heat inserts
hinge of the light holder | printedpart | 1
M3 HEX key | tool | 1
M3 nut | part | 14
M3x10 screw | part | 15 | Screw
M3x15 screw | part | 4 | Screw
M3x20 HEX screw | part | 1 | M3 HEX screw
M3x20 X screw | part | 1 | M3 X Screw
M3x5 screw | part | 2
main knob | printedpart | 1
middle plate | lasercutpart | 1
nut pusher | printedtool | 1
O ring | part | 1
piler | tool | 1
screen cover | printedpart | 1
screw washers | part | 2
screwdriver | tool | 1
short base legs | printedpart | 4
slide knob | printedpart | 1
sliding piece of the light holder | printedpart | 1
soldering iron | tool | 1
Stl files | stl | 1
top piece | printedpart | 1
upper legs | printedpart | 4
upper plate | lasercutpart | 1

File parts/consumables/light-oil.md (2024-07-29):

# Light oil

A component that lubricates the mechanism to make it work more smoothly.



*Supplier:* [Sodimac](https://www.sodimac.cl/sodimac-cl/articulo/110368264/Lubricante-multiuso-para-auto-89-ml/110368269)

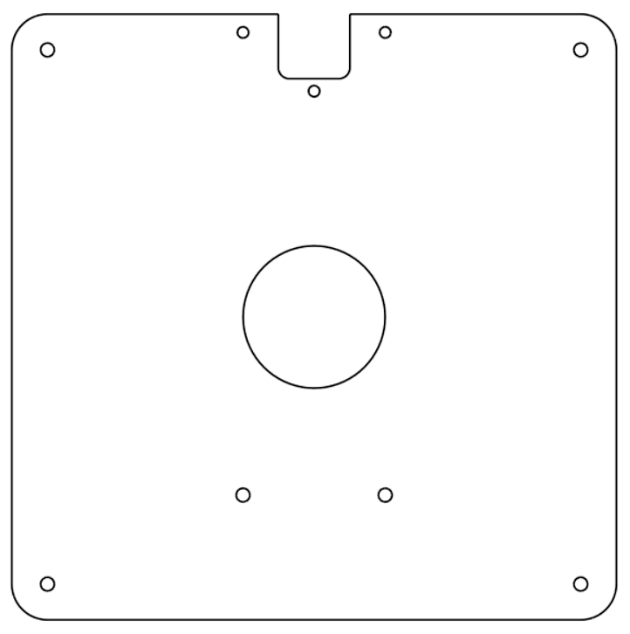
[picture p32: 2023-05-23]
parts/materials/laser-cut/top-plate.png

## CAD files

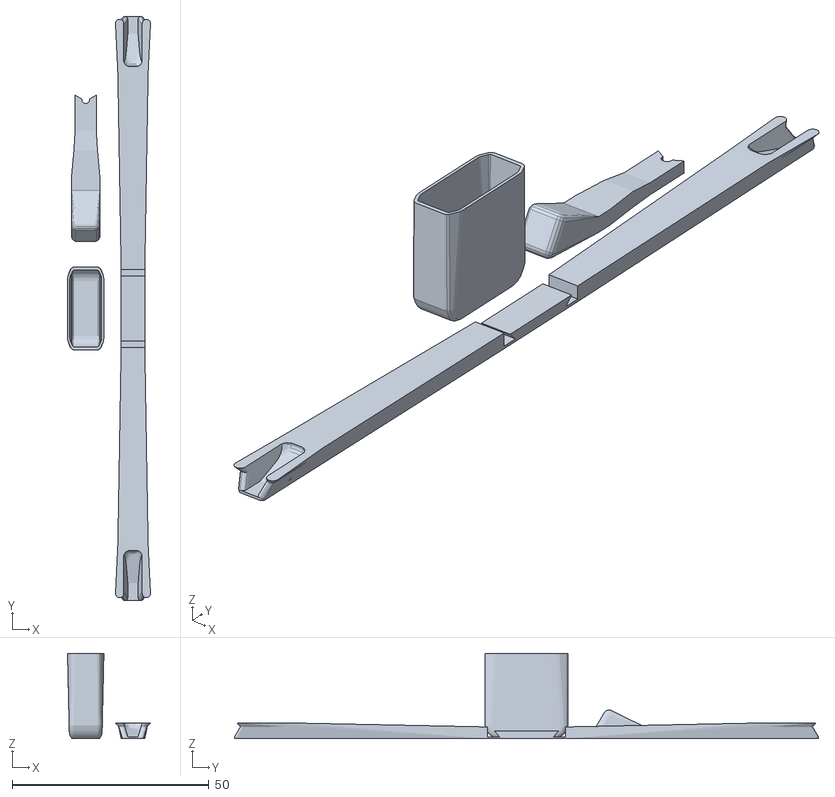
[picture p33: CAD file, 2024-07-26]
models/actuator-assembly-tools.stl
21.1 x 148.2 x 21.7

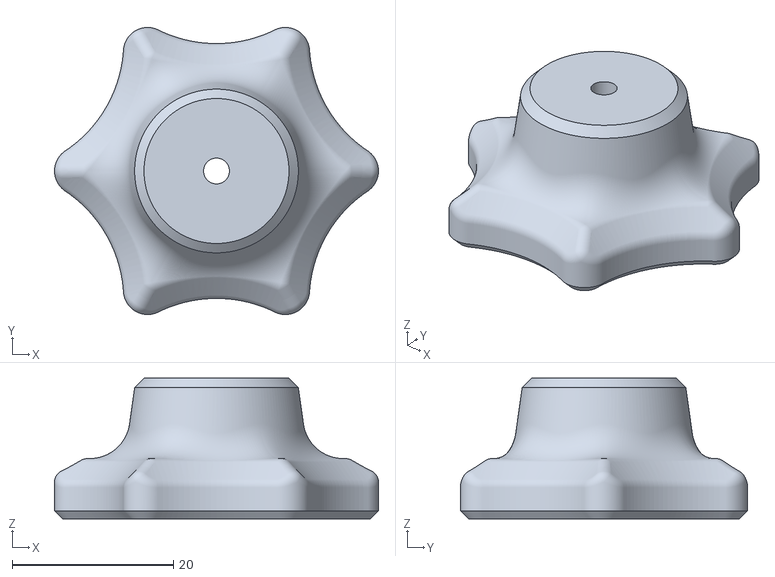
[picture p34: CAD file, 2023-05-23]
models/mainknob.stl
40.2 x 35.6 x 17.5

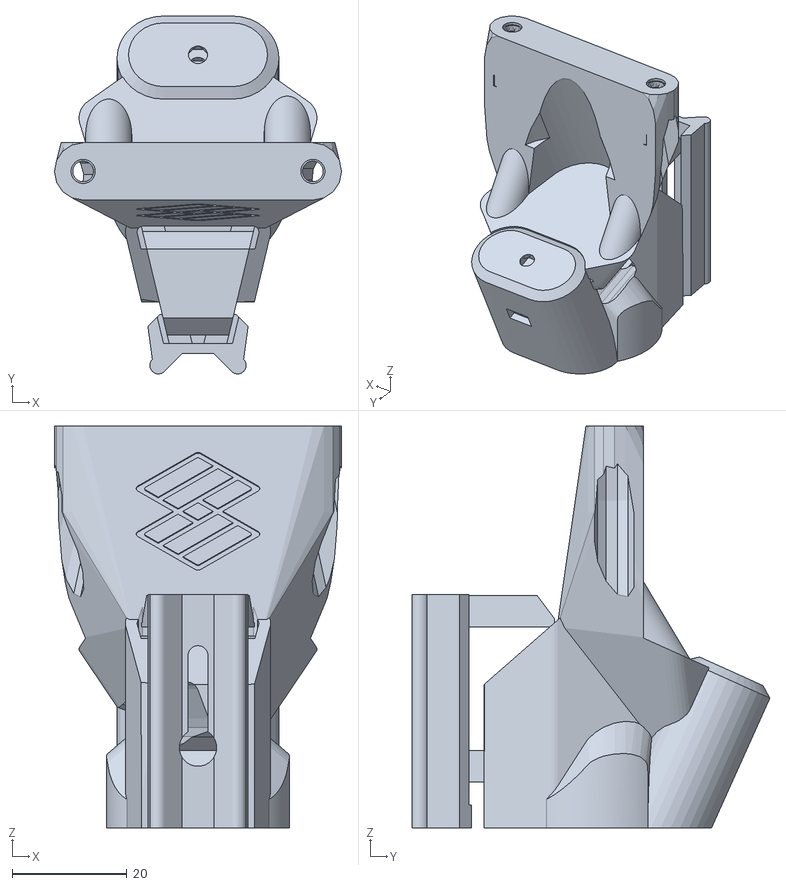
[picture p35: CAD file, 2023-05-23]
models/focusing-assembly.stl
50.0 x 62.3 x 70.0

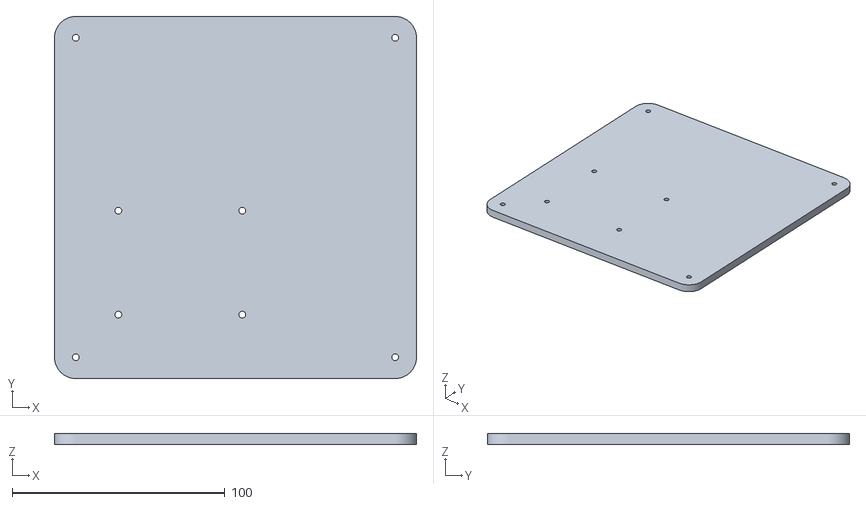
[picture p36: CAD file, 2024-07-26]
models/Holders-bottom-plate.stl
170.0 x 170.0 x 5.00

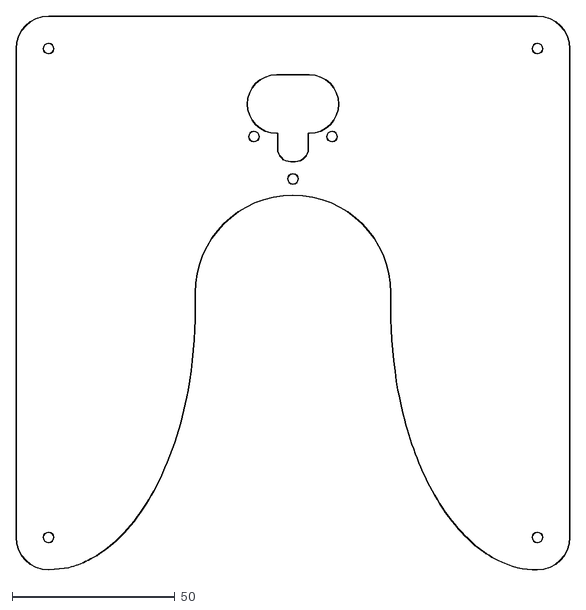
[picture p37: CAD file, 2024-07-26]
parts/materials/laser-cut/middle-plate.dxf
170.0 x 170.0

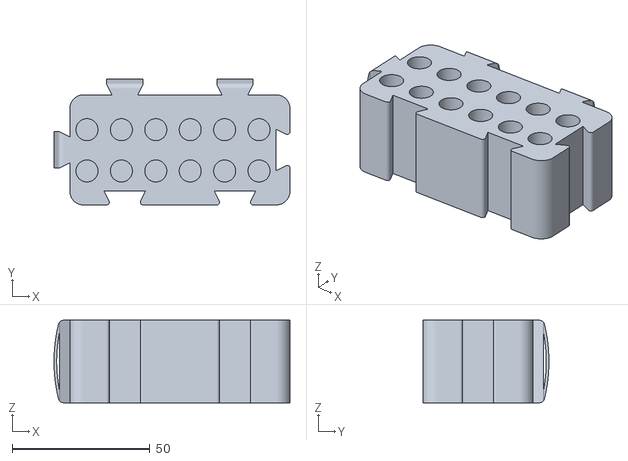
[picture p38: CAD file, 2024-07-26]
variants/models/0.6ml-double.stl
85.7 x 45.7 x 30.0

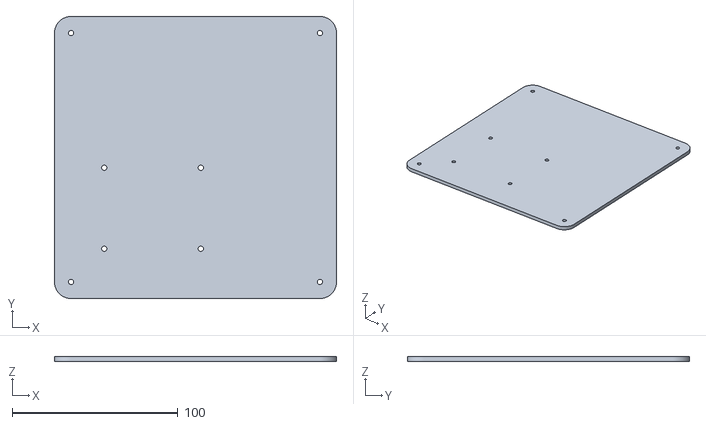
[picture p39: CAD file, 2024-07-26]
models/3D-Bottom-plate.stl
170.0 x 170.0 x 3.00

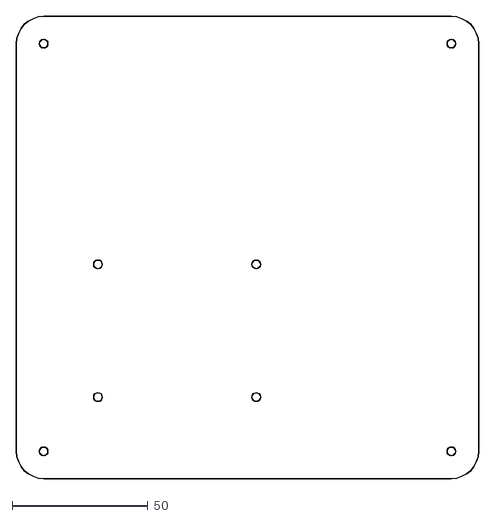
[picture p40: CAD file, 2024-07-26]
parts/materials/laser-cut/bottom-plate.dxf
170.0 x 170.0

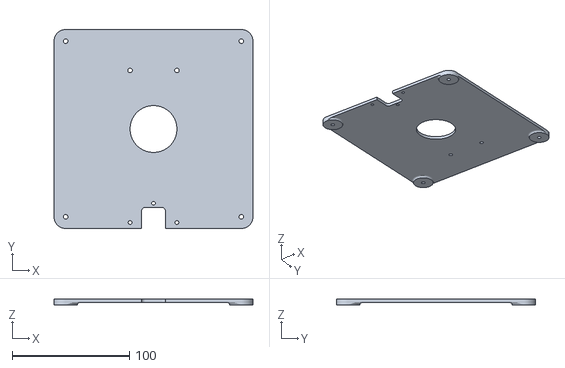
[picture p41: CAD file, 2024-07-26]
variants/models/3d-top-plate.stl
170.0 x 170.0 x 5.00

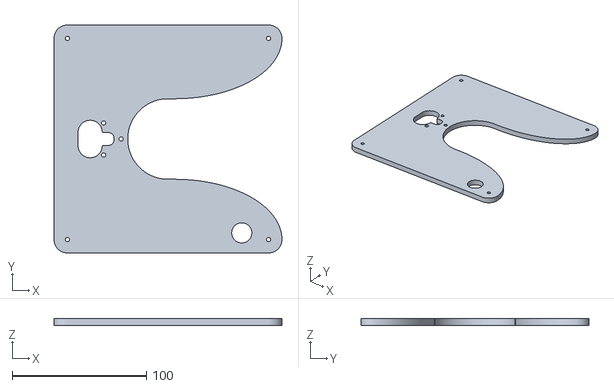
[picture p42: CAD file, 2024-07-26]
models/Holders-middle-plate.stl
170.0 x 170.0 x 5.00

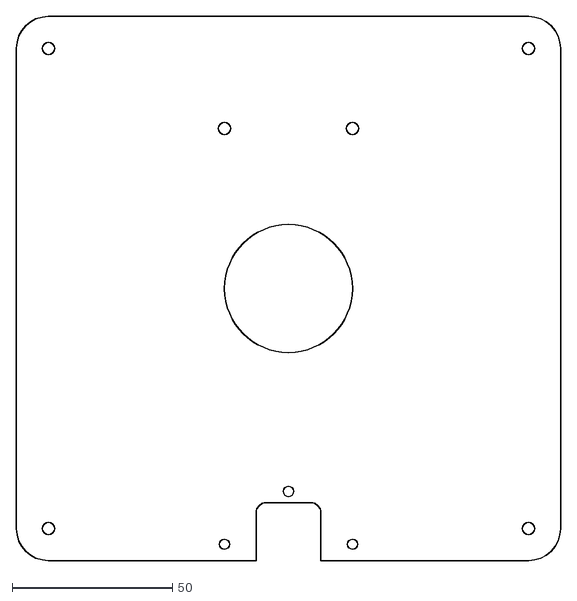
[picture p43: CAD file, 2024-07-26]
parts/materials/laser-cut/top-plate.dxf
170.0 x 170.0

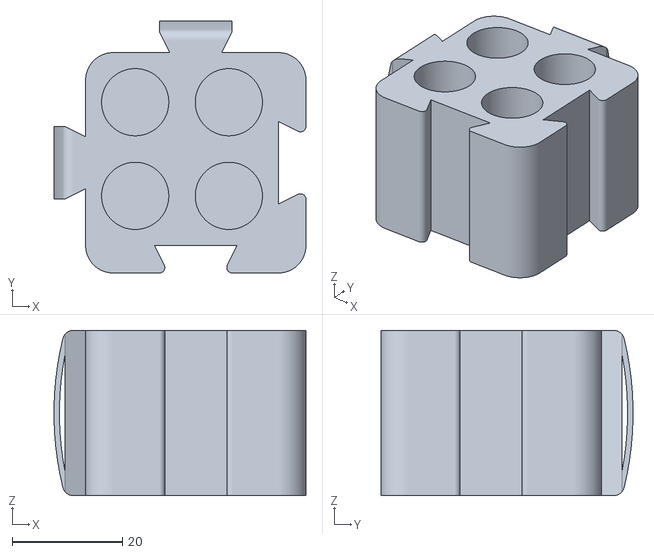
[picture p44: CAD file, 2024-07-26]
variants/models/Cryo-vial-single.stl
45.7 x 45.7 x 30.0

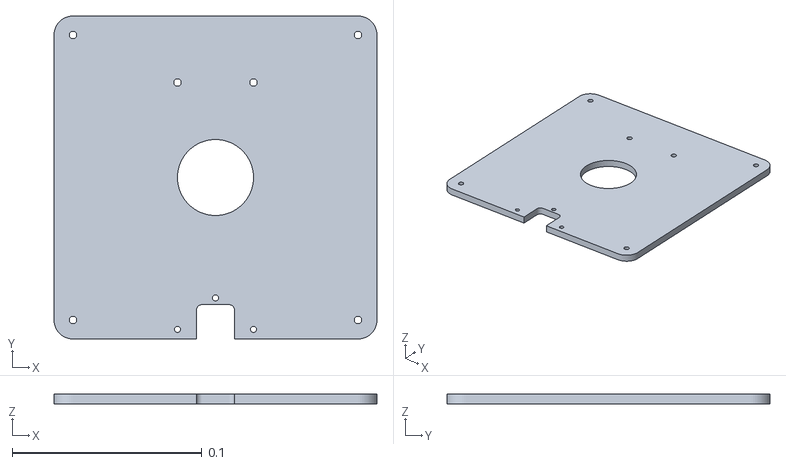
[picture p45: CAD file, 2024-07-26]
models/top-plate.stl
0.17 x 0.17 x 0.005

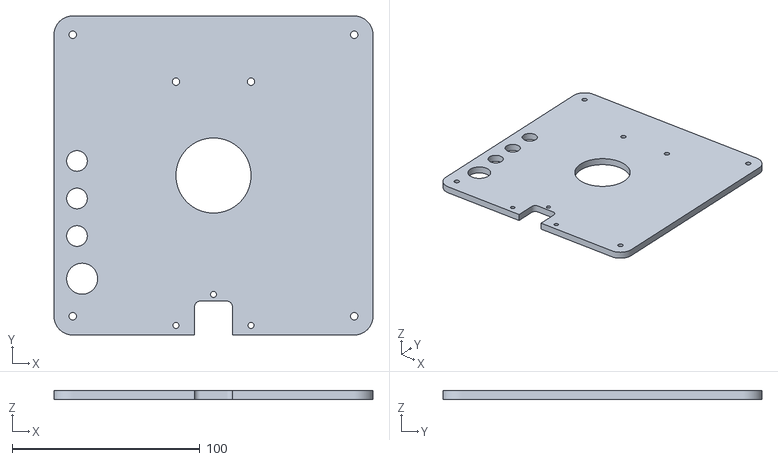
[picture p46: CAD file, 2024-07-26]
variants/models/custom-top-plate.stl
170.0 x 170.0 x 5.00

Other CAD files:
models/leg_test.stl
variants/models/3d-middle-plate.stl
models/middle-plate.stl
variants/models/0.2ml-double.stl
models/arm-pin.stl
models/basefocusing.stl
models/camera-platform.stl
models/foot-M.stl
models/illumination-base.stl
models/illumination-slider.stl
models/illumination-thumbscrew.stl
models/led-arm.stl
models/led-cover.stl
models/lens-spacer.stl
models/slideknob.stl
models/spacer-11mm.stl
models/spacer-4mm.stl
models/standoff-M.stl
models/standoff-S.stl
models/thumbwheel.stl
models/z_foot.stl
variants/models/1.5ml-single.stl
variants/models/15ml-single.stl
variants/models/25mm-heatsink-cover.stl
variants/models/25mm-heatsink-spacer.stl
variants/models/3d-screen-base.stl
variants/models/3d-screen-case.stl
variants/models/3d-screen-top.stl
variants/models/50ml-single.stl
variants/models/Cuvettes-double-thicker.stl
variants/models/Cuvettes-double-thinner.stl

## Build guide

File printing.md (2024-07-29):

# Print the plastic parts

{{BOM}}

[PLA filament]: parts/materials/pla_filament.md "{cat:material}"
[Black PLA filament]: parts/materials/black_pla_filament.md "{cat:material}"
[RepRap-style printer]: parts/tools/rep-rap.md "{cat:tool}"
[Precision wire cutter]: parts/tools/precision-wire-cutters.md "{cat:tool}"
[Utility knife]: parts/tools/utility-knife.md "{cat:tool}"
[leg test]:models/leg_test.stl "{previewpage}"

## Set your printer settings {pagestep}

Almost all station parts can be printed out of [PLA filament] on most [RepRap-style printers][RepRap-style printer]{qty:1}.

We recommend the following printer settings:

|Setting        |Value          |
|------------   |--             |
|Material       |PLA            |
|Material Temperature |Recommended by the PLA brand|
|Layer height   |0.2mm or less  |
|Infill         |Printer default or more|
|Brim           |Recommended for all parts|
|Slice gap closing radius |0.001mm |

Test whether your printer can print the pieces for this station or other open-source designs. Download and print the [leg test] file. This will only use about [5 grams of PLA][PLA filament]{qty: 5g}.

The result should look like this (this has been printed with a brim):

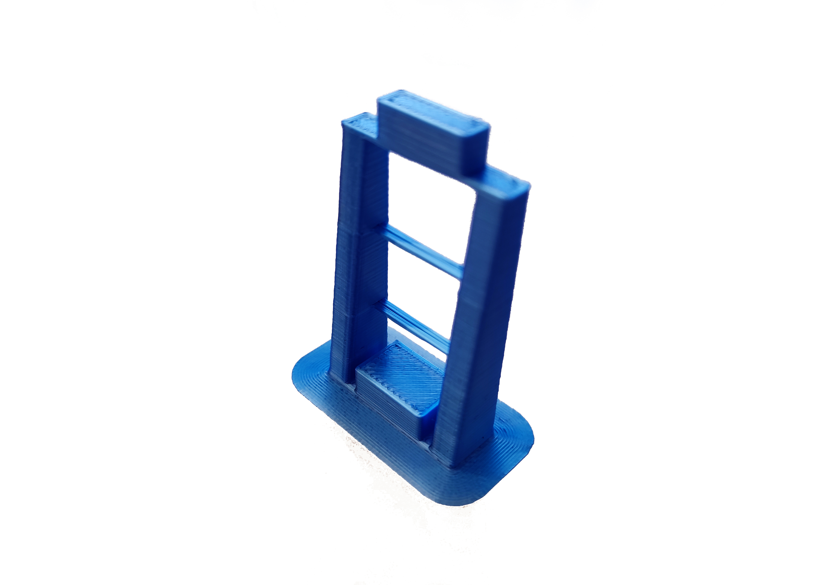
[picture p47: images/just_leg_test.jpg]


As a general rule, strength is more important than surface finish, so very thin layers (less than 0.15mm or so) are unlikely to result in a station that performs any better, though it may improve the appearance.

##Download and Printing {pagestep}

Now that you have tested your [3D printer][RepRap-style printer] and [filament][PLA filament]{qty: 200g, note: "Of any color you want"} you can print the plastic parts:

You can have access to all the STLs in [**Printables**](https://www.printables.com/model/647564) or go for free to our [**Online CAD software**](https://cad.onshape.com/documents/56f3731ad1d54872e3d730b5/w/79a6f9b65ec1b22fe0bc7f1a/e/d497faac00a6e40fe8fec4e7) to make your own version. You can also download them individually here:

* Actuator assembly tools ([nut tool]{output,qty:1}, [band tool]{output,qty:1}, and [band tool cover]{output,qty:1}): [actuator_assembly_tools.stl](models/actuator-assembly-tools.stl){previewpage}
* [Focusing assembly]{output,qty:1}: [focusing-assembly.stl](models/focusing-assembly.stl){previewpage}
* [Actuator Foot]{output,qty:1}: [z_foot.stl](models/z_foot.stl){previewpage}
* [Thumbwheel]{output,qty:1}: [thumbwheel.stl](models/thumbwheel.stl){previewpage}
* [Pi camera platform]{output,qty:1}: [camera-platform.stl](models/camera-platform.stl){previewpage}
* [Lens spacer]{output,qty:1}: [lens-spacer.stl](models/lens-spacer.stl){previewpage} - **This must be printed in [black][Black PLA filament]{qty: 50g}!**
* [Illumination base]{output,qty:1}: [illumination-base.stl](models/illumination-base.stl){previewpage} - **This must be printed with supports**
* [Illumination slider]{output,qty:1}: [illumination-slider.stl](models/illumination-slider.stl){previewpage}
* [Illumination thumbscrew]{output,qty:1}: [illumination-thumbscrew.stl](models/illumination-thumbscrew.stl){previewpage}
* [Illumination arm]{output,qty:1}: [led-arm.stl](models/led-arm.stl){previewpage} - **This must be printed with supports**
* [Hinge pin]{output,qty:1}: [arm-pin.stl](models/arm-pin.stl){previewpage}
* [LED cover]{output,qty:1}: [led-cover.stl](models/led-cover.stl){previewpage}
* [Standoff-S]{output,qty:4}: [standoff-S.stl](models/standoff-S.stl){previewpage}
* [Standoff-M]{output,qty:4}: [standoff-M.stl](models/standoff-M.stl){previewpage}
* [Foot-M]{output,qty:4}: [foot-M.stl](models/foot-M.stl){previewpage}
* [Spacer-S]{output,qty:4}: [spacer-4mm.stl](models/spacer-4mm.stl){previewpage}
* [Spacer-M]{output,qty:2}: [spacer-11mm.stl](models/spacer-11mm.stl){previewpage}

## Clean-up of printed parts {pagestep}

>!! **Be careful when removing the brim:** To avoid injury, first remove the bulk of the brim without a knife. Remove the remaining brim with a peeling action as described below.

Carefully remove the printing brim from all parts. To remove brim:

1. Use [precision wire cutters][Precision wire cutter]{qty: 1} to remove most of the brim from the part.
2. Clean up the remaining brim with a [utility knife][Utility knife]{qty: 1, note: "Not a scalpel!"}:
    * Hold the knife in your dominant hand with 4 fingers curled around the handle, leaving your thumb free.
    * Hold the part in your other hand, as far away from the surface, to be cut as possible.
    * Support the part with the thumb of your dominant hand.
    * Place the blade on the surface to be cut, and carefully close your dominant hand, moving the blade, under control, towards your thumb.

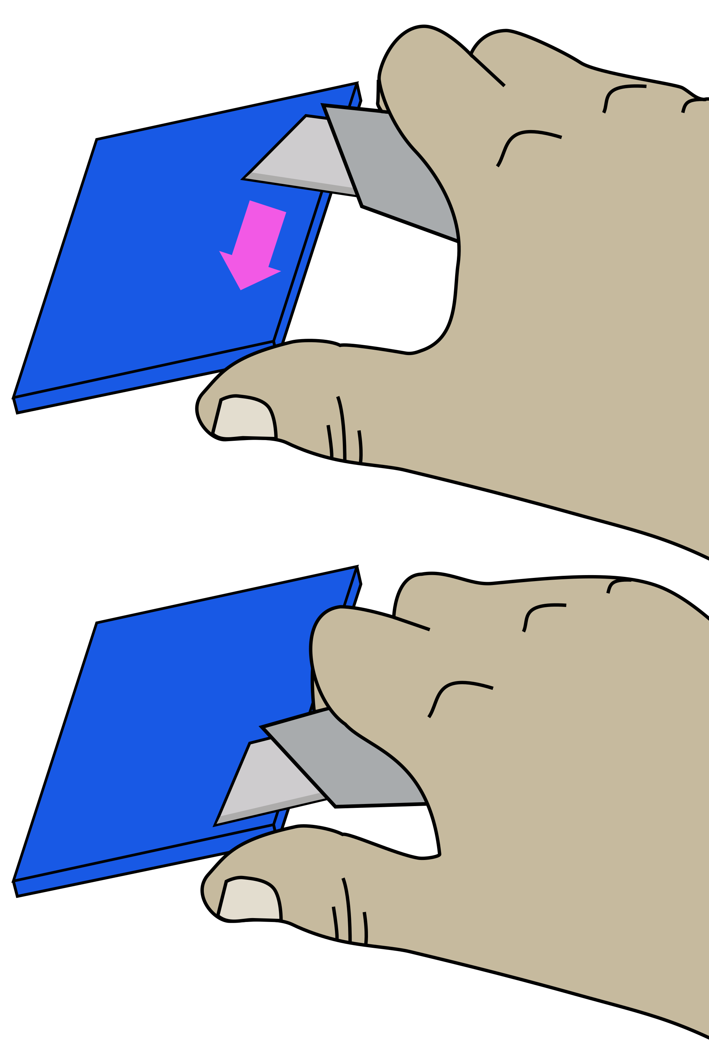
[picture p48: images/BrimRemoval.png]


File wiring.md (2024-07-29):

# Mount the electronics

{{BOM}}

[M3x25mm cap head screw]: parts/mech/M3-25.md "{cat:mechanic}"
[M3 nut]: parts/mech/nuts.md "{cat:mechanic}"
[Raspberry Pi]: parts/elect/rpi-v4.md "{cat:electronic}"
[Pi HAT]: parts/elect/pi-hat.md "{cat:electronic, note:'This is a custom open-source board documented [here](https://github.com/wenzel-lab/modular-microfluidics-workstation-controller/tree/master/module-pi)'}"
[Strobe Module]: parts/elect/strobe-module.md "{cat:electronic, note:'This is a custom open-source board documented [here](https://github.com/wenzel-lab/modular-microfluidics-workstation-controller/tree/master/module-fast-imaging)'}"
[Strobe Cable]: parts/elect/strobe-cable.md "{cat:electronic, note:'This is a custom connector documented [here](https://github.com/wenzel-lab/open-microfluidics-workstation/)'}"
[Needle-nose plier]: parts/tools/pliers.md "{cat:tool}"
[2.5mm Ball-end Allen key]: parts/tools/2.5mmBallEndAllenKey.md "{cat:tool}"
[Spacer-S]: models/spacer-4mm.stl "{previewpage}"
[Spacer-M]: models/spacer-11mm.stl "{previewpage}"
[Nitrile gloves]: parts/consumables/gloves.md "{cat:consumable}"

These instructions assume you have the custom electronic components pre-assembled.

>! **Caution!** The electronic boards are static sensitive. Before touching them, touch a metal-earthed object. If you own one, consider wearing an anti-static strap.

## Connect the camera {pagestep}

* Use [nitrile gloves][Nitrile gloves]{Qty:2} to manipulate electronic components. 
* Insert the ribbon cable from the optics module into the camera port of the [Raspberry Pi]{qty:1}, ensuring the contacts are on the opposite side of the clasp. There are [detailed instructions on the Raspberry Pi website](https://projects.raspberrypi.org/en/projects/getting-started-with-picamera/2).

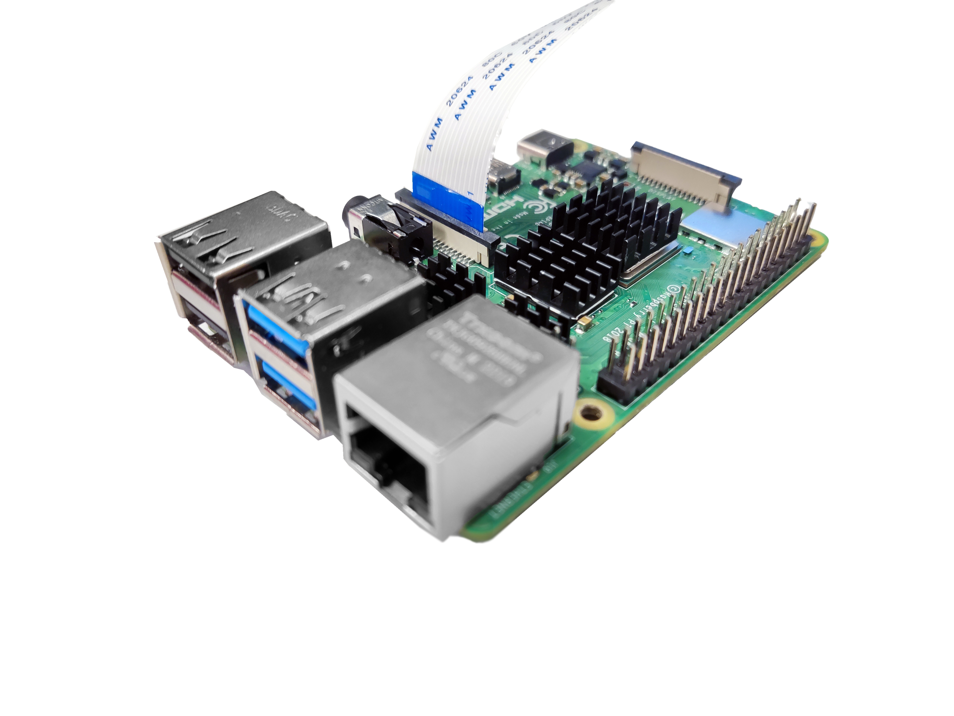
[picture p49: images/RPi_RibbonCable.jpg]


## Prepare the electronics {pagestep}

* Place the [strobe module][Strobe Module]{qty:1} over the [Pi HAT]{qty:1}.
* Mount the Pi HAT on the Raspberry Pi GPIO headers. There is a space to place the ribbon cable.

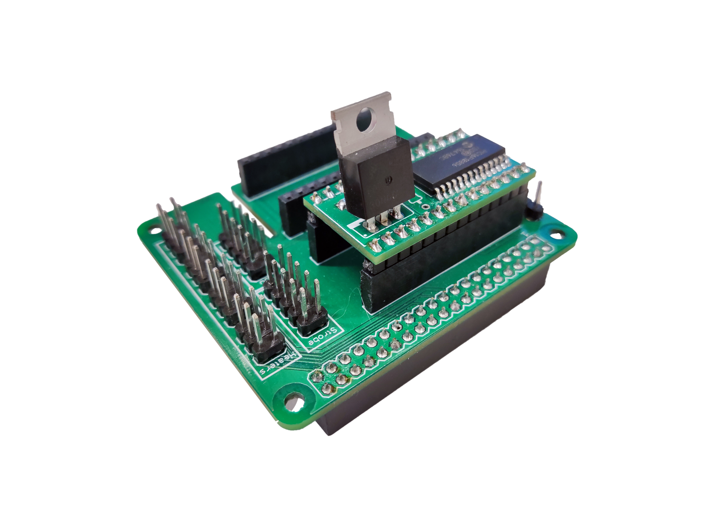
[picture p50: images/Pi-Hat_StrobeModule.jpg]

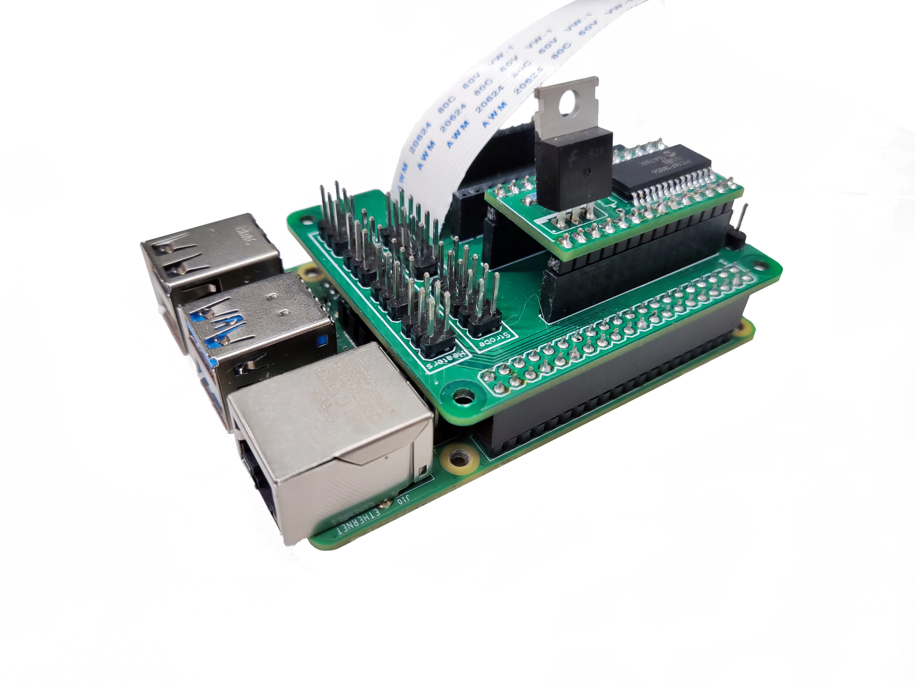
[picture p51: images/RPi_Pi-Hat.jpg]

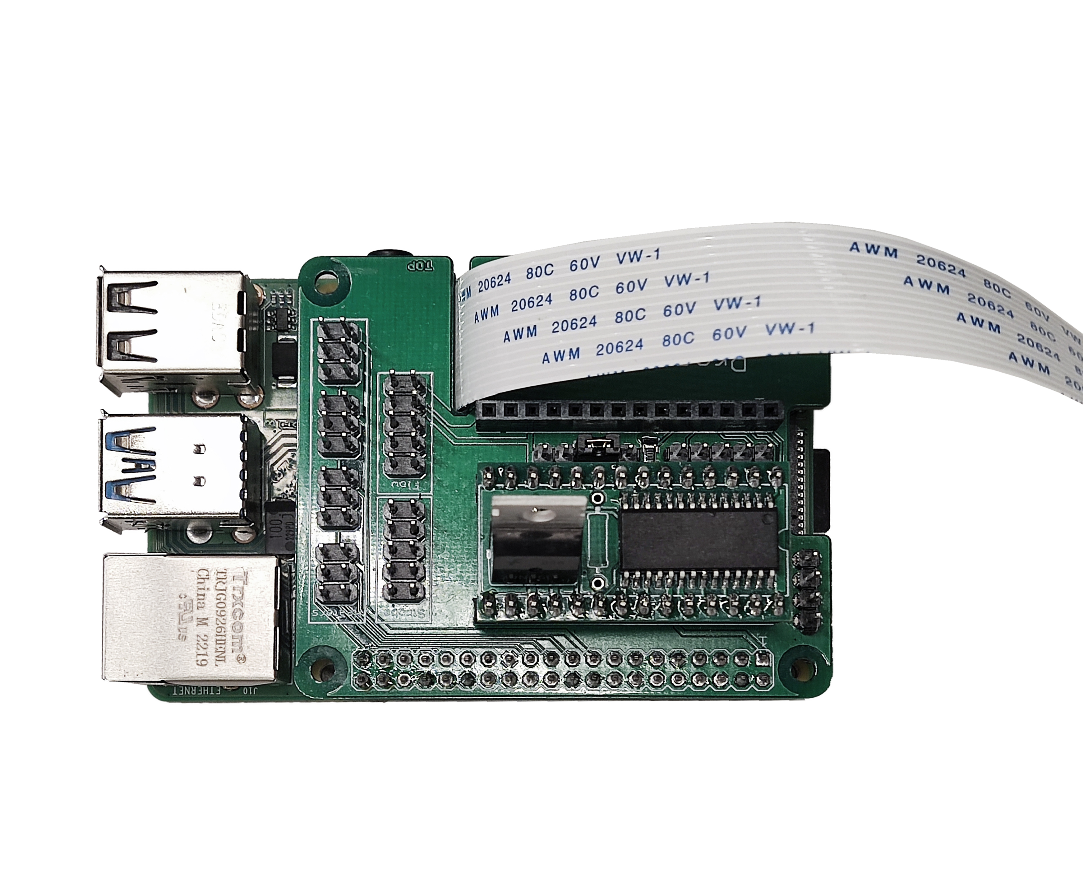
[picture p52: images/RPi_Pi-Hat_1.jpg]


* Connect the 5-pin double row DuPont female connector of the [strobe cable][Strobe Cable]{qty:1} to the Pi HAT.

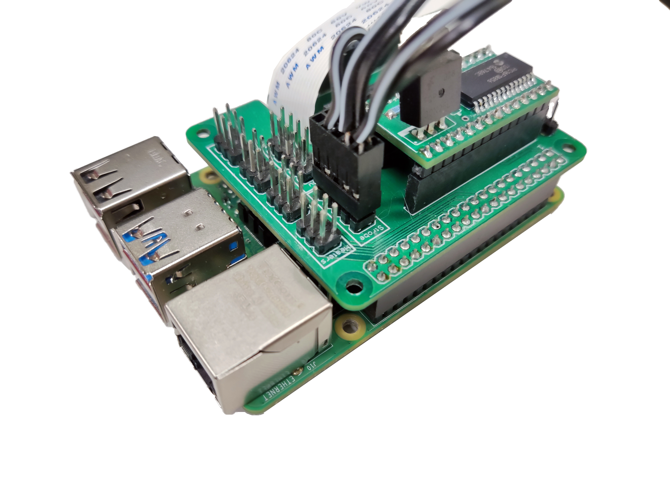
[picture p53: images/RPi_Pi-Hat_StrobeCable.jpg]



## Mount the boards {pagestep}

* Take four [M3x25mm cap head screws][M3x25mm cap head screw]{qty: 4} and insert them into each hole from the Pi hat and the Raspberry Pi. Use a [2.5mm Ball-end Allen key]{qty:1}.
* Use a [11mm spacer][Spacer-M](fromstep){qty: 2, cat:printedpart} in between the holes next to the power supply and USB connectors. A [needle-nose plier][Needle-nose plier]{qty:1} can be helpful to hold the spacer while you screw.

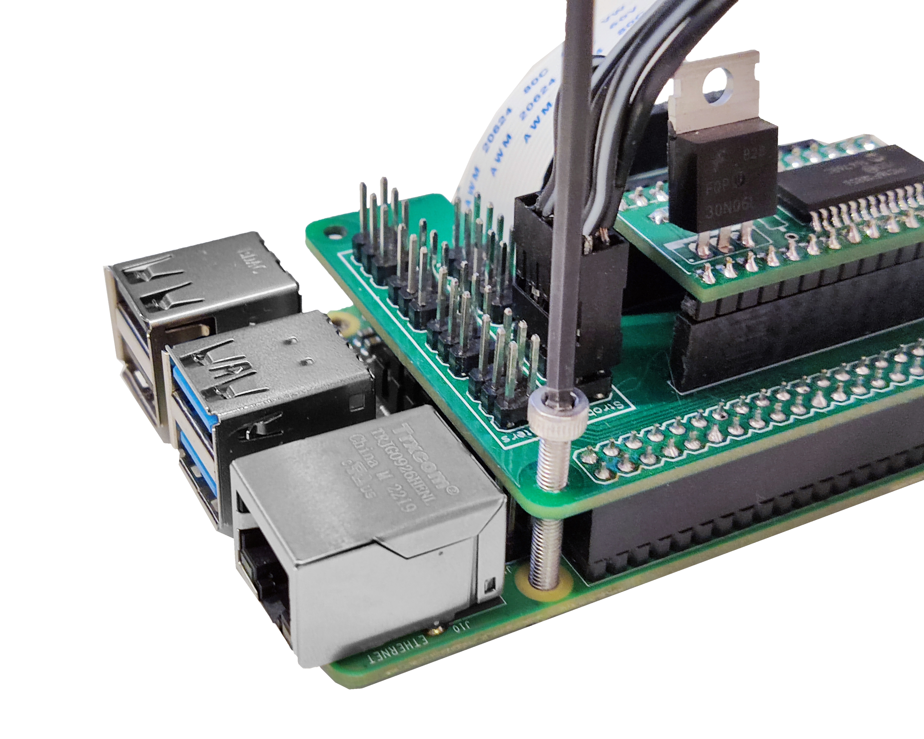
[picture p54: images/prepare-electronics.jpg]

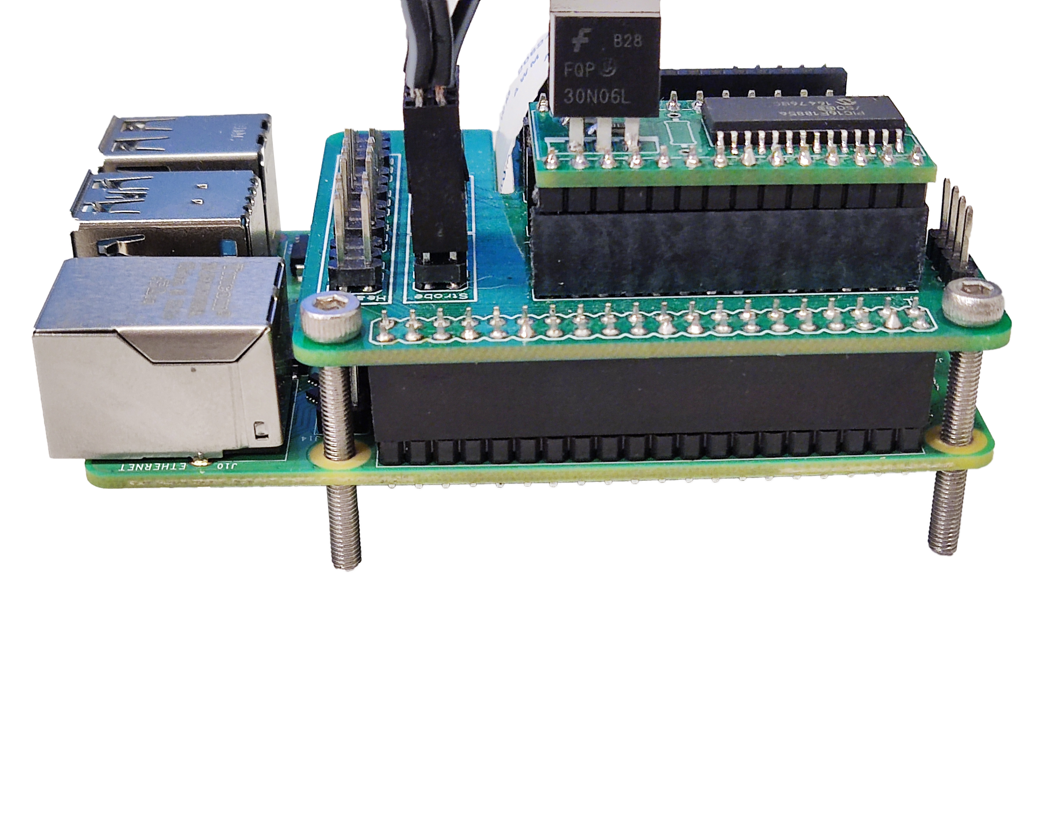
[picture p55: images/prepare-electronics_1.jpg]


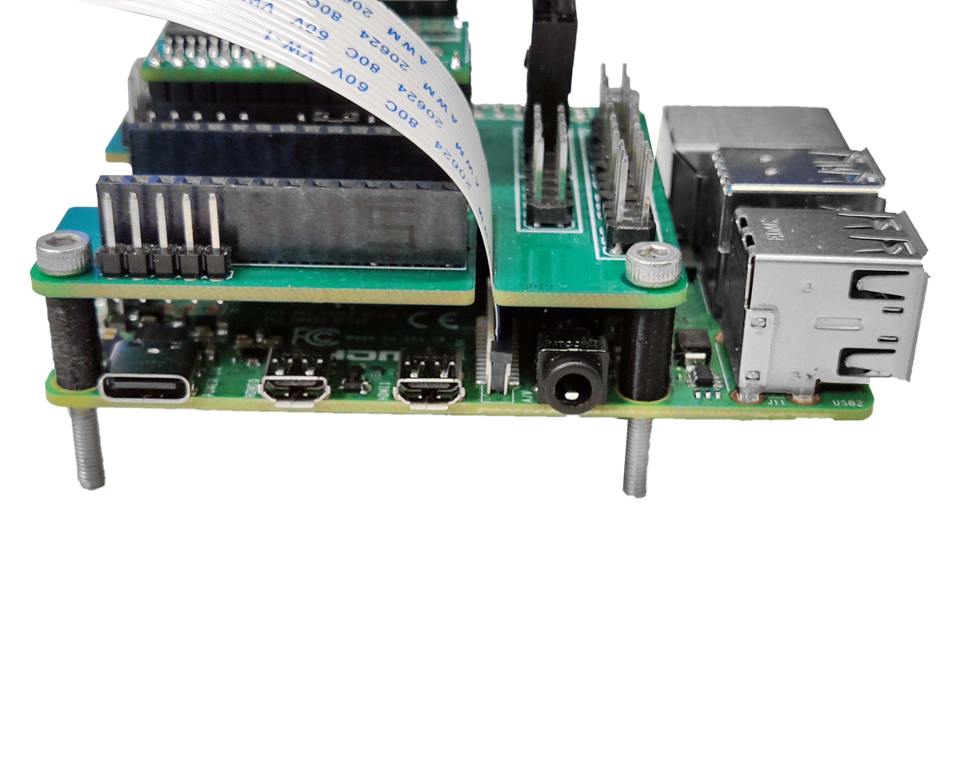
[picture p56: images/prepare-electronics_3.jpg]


* Use a [4mm spacer][Spacer-S](fromstep){qty: 4, cat:printedpart} in between the electronic assembly and the bottom plate.
* Place the electronic assembly in the bottom plate and attach it to the surface using four [M3 nuts][M3 nut]{qty: 4}. A [needle-nose plier][Needle-nose plier] can be helpful to hold the nut.

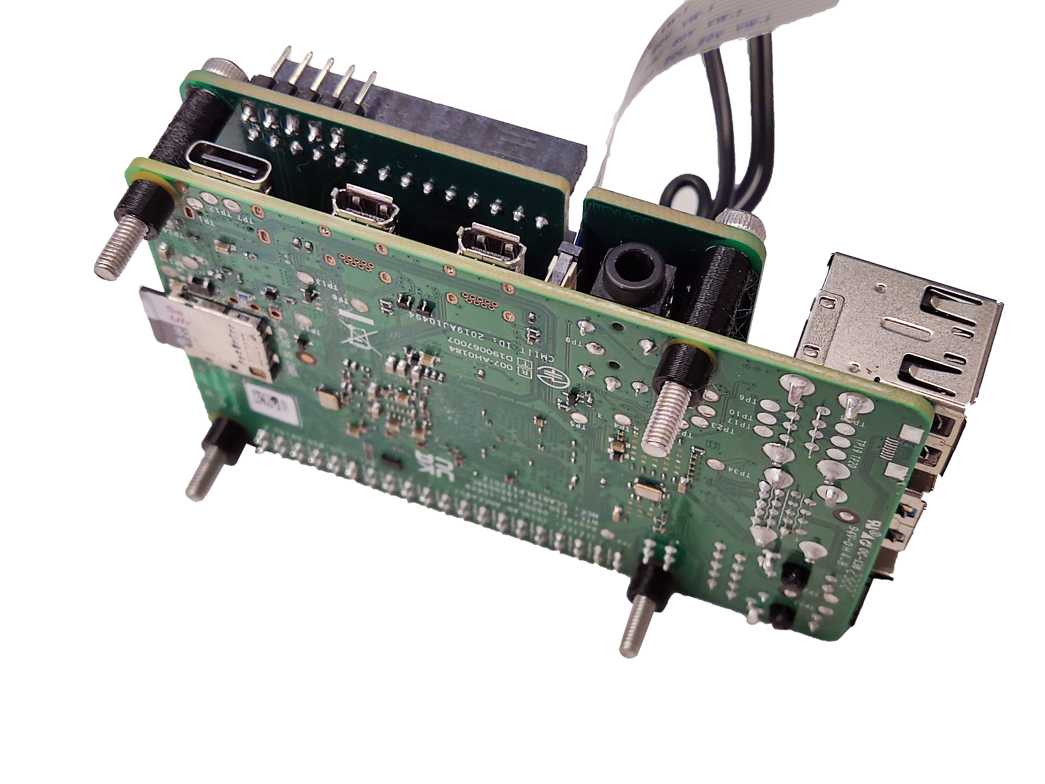
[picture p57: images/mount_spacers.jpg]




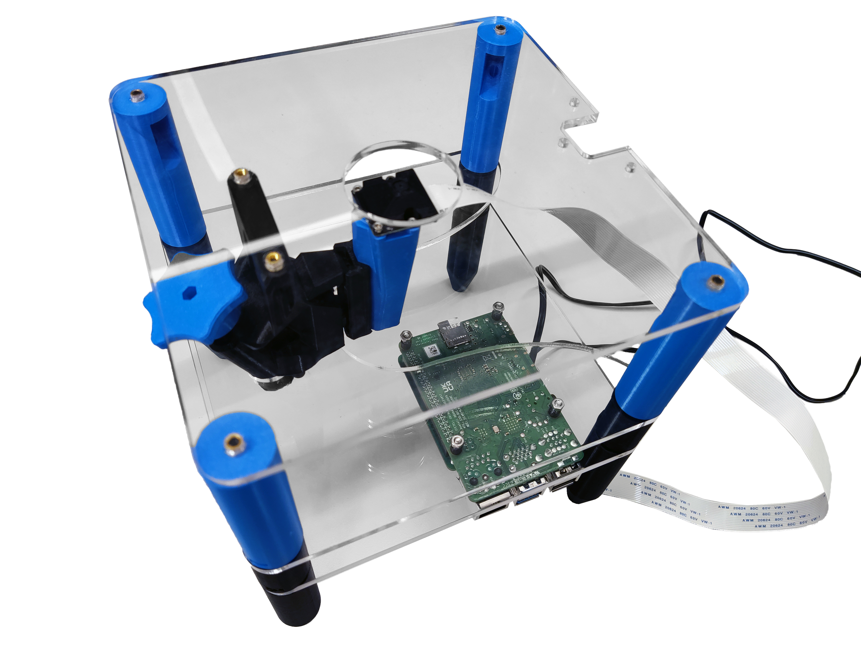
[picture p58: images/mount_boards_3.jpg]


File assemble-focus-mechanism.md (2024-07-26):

# Assemble the focus mechanism

{{BOM}}

[M3x25mm hex head screw]: parts/mech/HEX-M3-25.md "{cat:mechanic}"
[M3 washers]: parts/mech/washer.md "{cat:mechanic}"
[light oil]: parts/consumables/light-oil.md "{cat:consumable, note:'Optional'}"
[M3 nut]: parts/mech/nuts.md "{cat:mechanic}"
[O-ring]: parts/mech/oring.md "{cat:mechanic}"
[Nut tool]: models/actuator-assembly-tools.stl "{previewpage}"
[Band tool]: models/actuator-assembly-tools.stl "{previewpage}"
[Thumbwheel]: models/thumbwheel.stl "{previewpage}"
[Focusing assembly]: models/focusing-assembly.stl "{previewpage}"
[Actuator Foot]: models/z_foot.stl "{previewpage}"

## Assemble the thumbwheel {pagestep}

* Push the [M3x25mm hex head screw]{qty:1} into the [thumbwheel][Thumbwheel](fromstep){qty:1, cat:printedpart}.
* Thread the [M3 washers]{qty:2} onto the screw.
* Place a drop of [light oil]{qty:1 drop} on the screw thread. You might want to put some kitchen paper or blu roll on your bench to soak up any dribbles of oil.

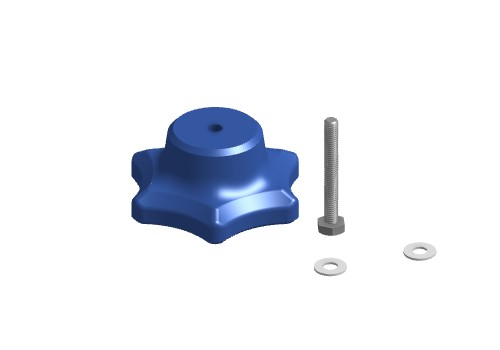
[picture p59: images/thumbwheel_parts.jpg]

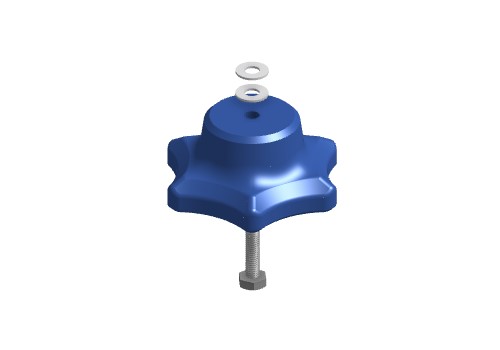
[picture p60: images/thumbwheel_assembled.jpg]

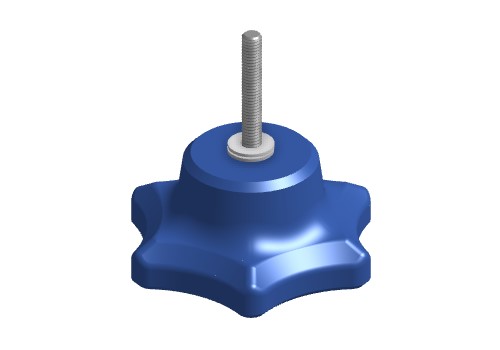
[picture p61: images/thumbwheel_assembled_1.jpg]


## Insert the nut {pagestep}

* Push the [M3 nut]{qty:1} into the slot in the [focusing assembly][Focusing assembly](fromstep){qty:1, cat:printedpart} (using the [nut insertion tool][Nut tool](fromstep){qty:1, cat:printedtool})

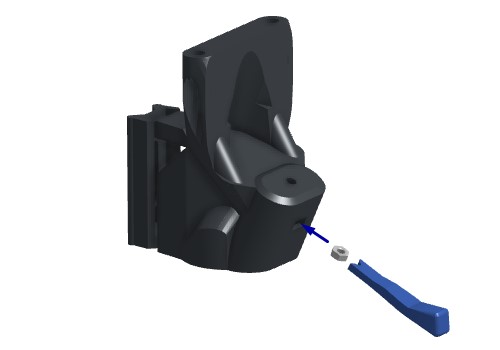
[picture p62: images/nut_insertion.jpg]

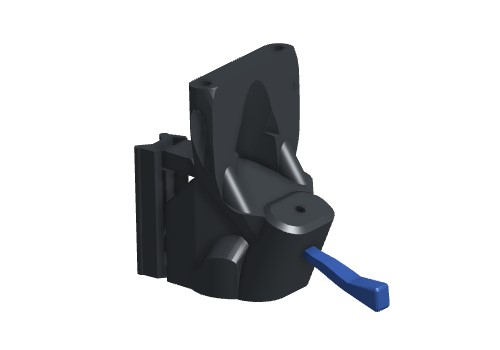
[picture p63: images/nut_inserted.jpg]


## Add the thumbwheel {pagestep}

* Screw the [thumbwheel][Thumbwheel] assembly into the [M3 nut] in the [focusing assembly][Focusing assembly].

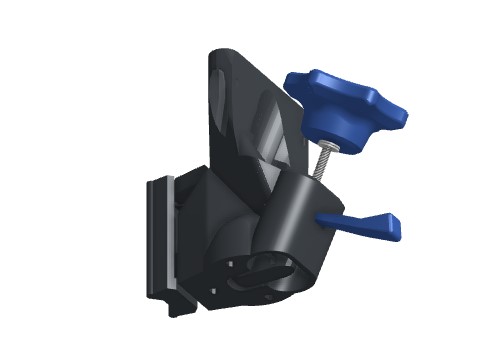
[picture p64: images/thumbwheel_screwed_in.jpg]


## Insert the O ring {pagestep}
* Next, we will insert the [O-ring] to complete the mechanism.

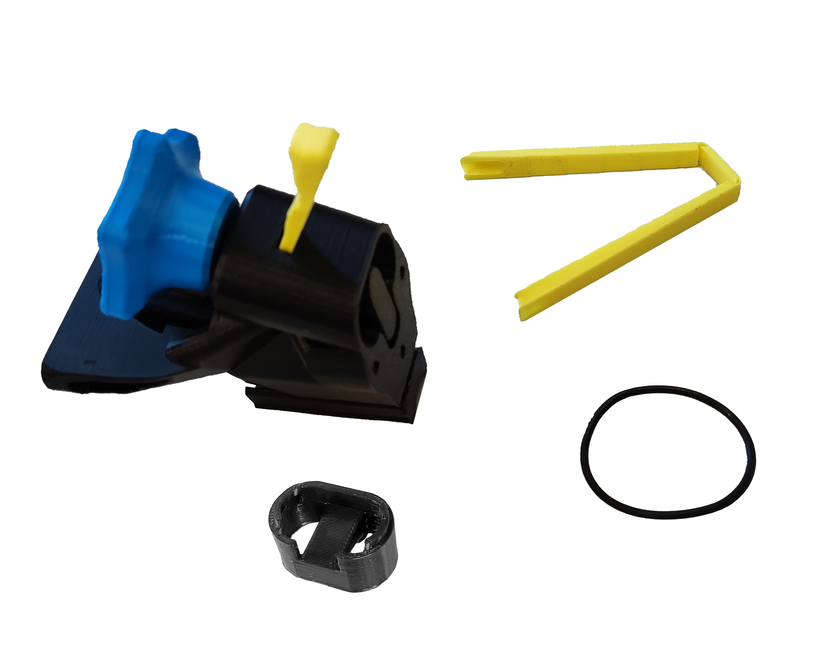
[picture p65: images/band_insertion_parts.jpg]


* Thread the [30mm diameter, 2mm thickness Viton O ring][O-ring]{qty:1} through the two holes in the [foot][Actuator Foot](fromstep){qty:1, cat:printedpart}, and use the [band insertion tool][Band tool](fromstep){qty:1, cat:printedtool} to stretch the two loops of band as shown in the picture.

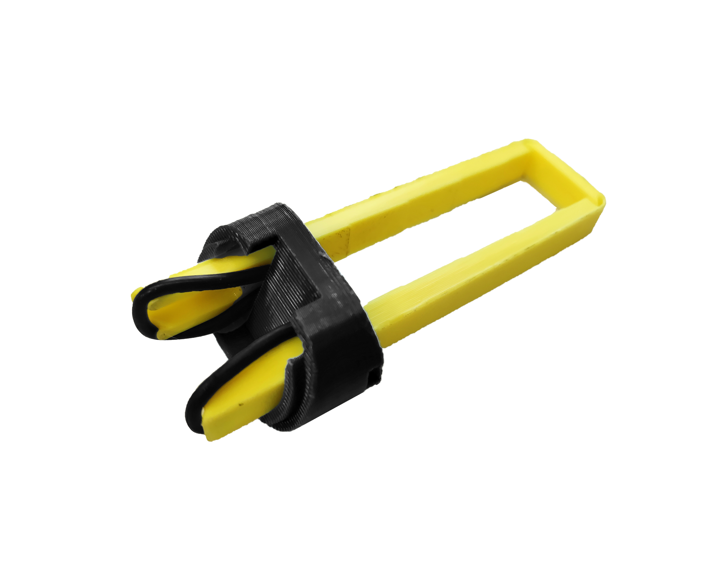
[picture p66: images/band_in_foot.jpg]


## Click the band into place {pagestep}

* Line the [foot][Actuator Foot] up with the hole in the bottom of the [focusing assembly][Focusing assembly], and push on the [band insertion tool][Band tool] to click the band into place.
* You should feel two clicks as the two ends of the band hook over the actuator column. It's easier if you use the [nut insertion tool][Nut tool] to hold the mechanism still as you do this.

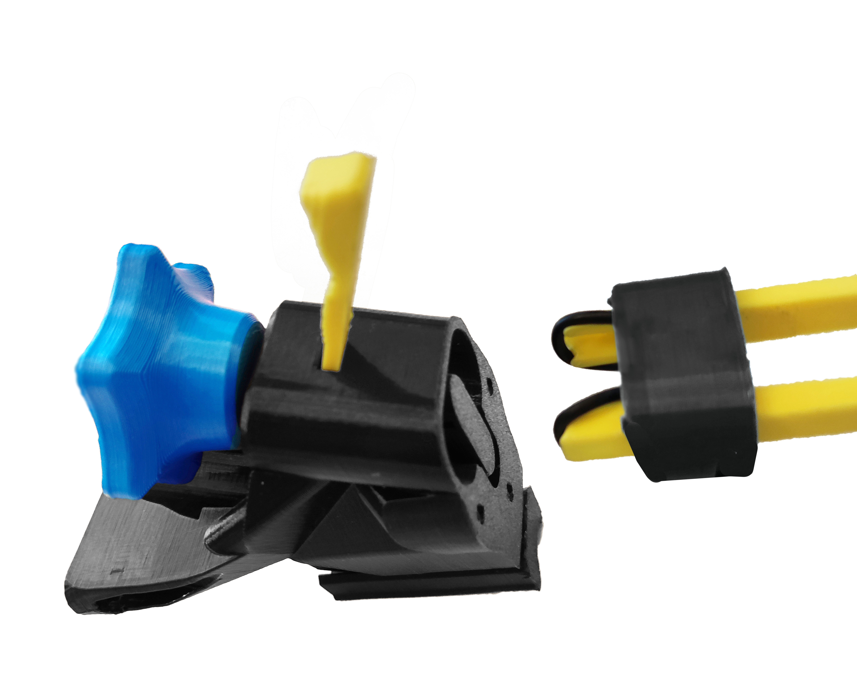
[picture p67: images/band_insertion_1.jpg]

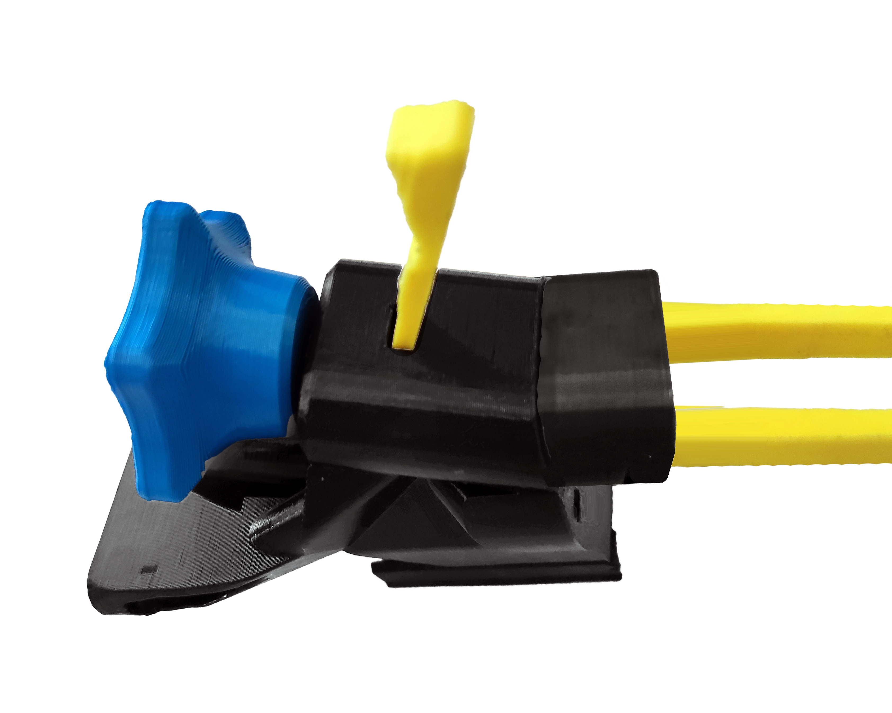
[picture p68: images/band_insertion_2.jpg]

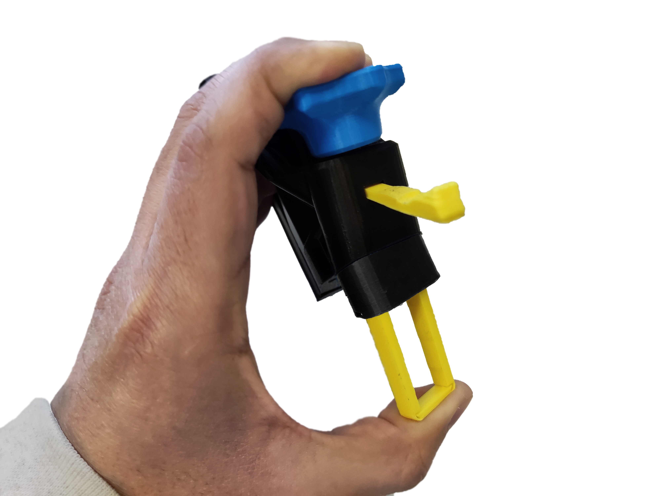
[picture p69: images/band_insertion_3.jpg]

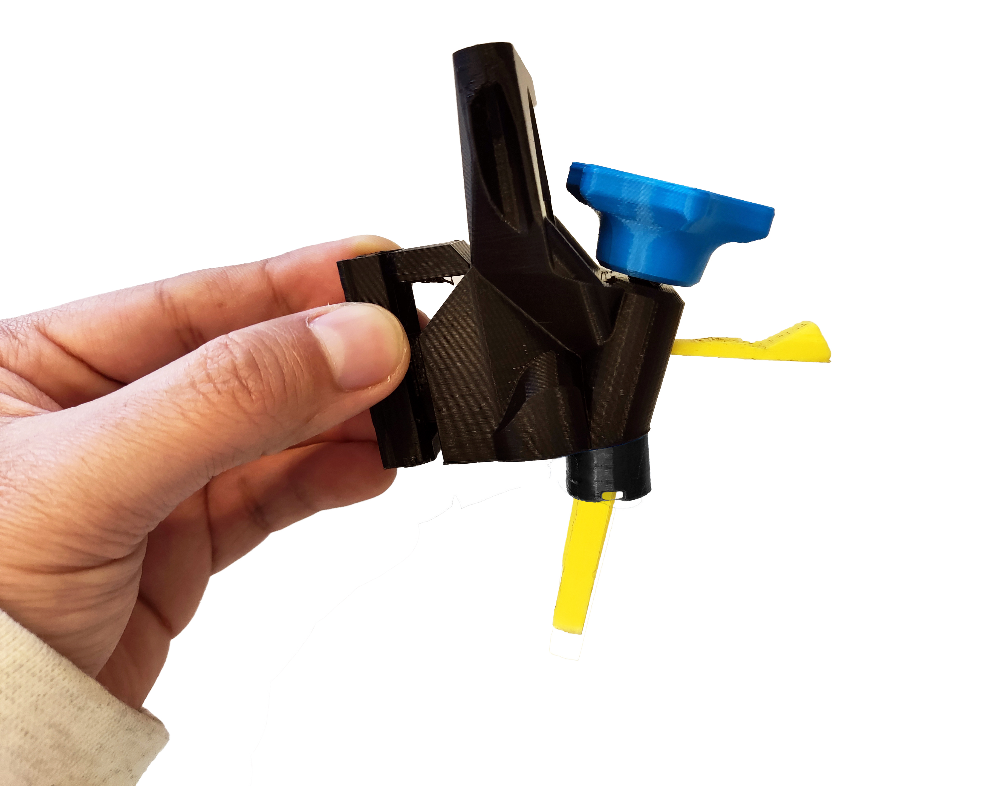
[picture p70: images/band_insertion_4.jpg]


## Remove the tool {pagestep}

* Gently pull the [band insertion tool][Band tool] out of the [foot][Actuator Foot].
* The band should pull the foot tight against the [focusing assembly][Focusing assembly] as shown.

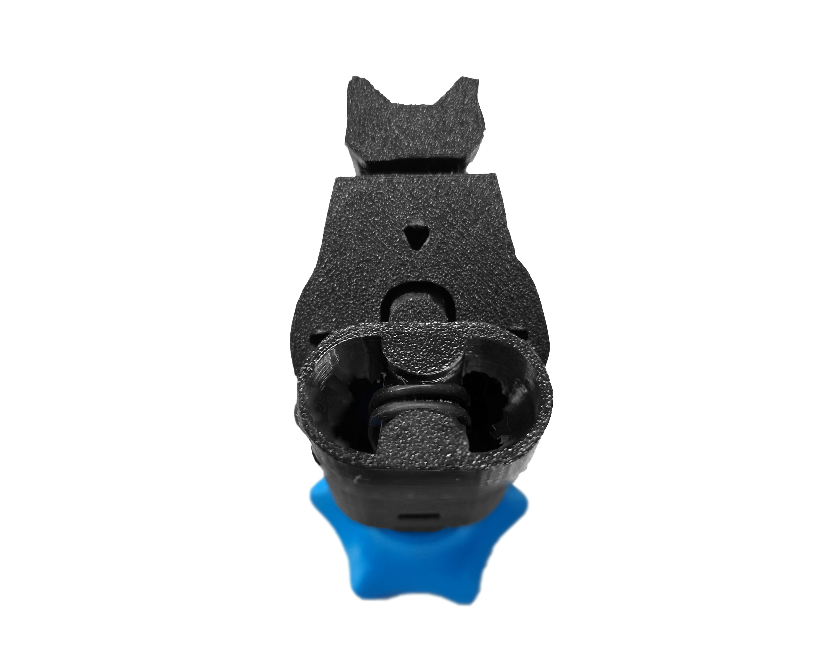
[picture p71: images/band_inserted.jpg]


Well done, you have now assembled the [focusing mechanism]{output, qty:1}.

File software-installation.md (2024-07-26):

# Software Installation

## Write your SD Card {pagestep}
You must install an operating system first to set up and use the Raspberry Pi board. Raspbian or Raspberry Pi OS is a Debian-based computer operating system for Raspberry Pi board. There are several OS versions for the workstation. Raspberry Pi OS 32-bit must be installed.
>i **Coming soon:** a pre-built SD card image that contains a full operating system with all the necessary software pre-installed. 

**Before you start, please get:**

* A computer with Internet
* A MicroSD card
* A SD card reader (OPTIONAL) 
* A SD card adapter (OPTIONAL)

**To write your MicroSD card:**

* Download the latest .img file from [Raspberry Pi website](https://www.raspberrypi.com/software/operating-systems/).
* Use an adapter to connect your MicroSD card to your computer.
* Use a program such as [Etcher](https://www.balena.io/etcher) or [Raspberry Pi imager](https://www.raspberrypi.com/software/) to flash the .img file onto your MicroSD card.

More detailed information on installing a Raspberry Pi operating system image onto an SD card can be found [here on the Raspberry Pi website](https://www.raspberrypi.com/documentation/computers/getting-started.html#installing-the-operating-system).

**First boot:**

Connect your Pi to a display, mouse, keyboard, and power. When the Pi first boots, you will be asked to complete a quick setup before rebooting.

Once you have installed and configured the Raspberry Pi OS, you can install the User Interface App.

## Enable SSH, SPI, and Camera {pagestep}

**Method 1:** Use the graphical tool "Raspberry Pi Configuration". This is found under Menu > Preferences > Raspberry Pi Configuration. Then you must select the "Interfaces" tab and set SSH, SPI, and Camera to "Enabled".

**Method 2:** From the command line or Terminal window, start by running `sudo raspi-config`. This will launch the raspi-config utility:

- Select “Interfacing Options”.
- Highlight the "SSH" option and activate **Select**.
- Select and activate **Yes**.
- Highlight and activate **Ok**.
- When prompted to reboot highlight and activate **Yes**.
- Repeat the previous steps to enable "SPI" and "Camera".

## Edit config.txt {pagestep}

We need to edit the config file `sudo nano /boot/config.txt`

Add `disable_camera_led=2` at the end of the file  

Then, save it with `CTL+O` > `Enter` > `CTL+X` and reboot the system `sudo reboot`.

## Plug in Camera {pagestep}

How to connect properly a Raspberry Pi camera and more information about the sensor can be found [here on the Raspberry Pi website](https://www.raspberrypi.com/documentation/accessories/camera.html). Use `vcgencmd get_camera` to verify if your camera was detected and `raspistill -o test.jpg` if it works.

>! Cameras are sensitive to static. Earth yourself before handling the PCB. A sink tap or similar should suffice if you don’t have an earthing strap.

## Install Libraries {pagestep}

The Python libraries that allow the Webb App to work on your Pi are the followings:

```
Flask 1.0.2
Flask-socketio 4.3.2
Werkzeug 0.14.1
Jinja2 2.10
Markupsafe 1.1.0
itsdangerous 0.24
eventlet 0.33.3
spidev 3.6
RPi.GPIO 0.7.1
picamera 1.13
Pillow 9.4.0
```
**Method 1:** Use the terminal window and install each of the above libraries with `pip install`. Example: `pip install Flask==1.0.2`

**Method 2:** Download [requirements.txt](https://github.com/wenzel-lab/open-microfluidics-workstation/blob/master/module-pi/requirements.txt) file and copy it into your Home folder on your Pi. Use the terminal window and install all the libraries with `pip install -r requirements.txt` 

>i Use `pip list` to verify which modules are installed and their versions. 

## Set up the GPIO pin states {pagestep}

GPIO pins states must be modified during the bootup sequence to use them with the peripherals of the workstation. Our own custom `dt-blob.bin` file specifies which pin states should change:

* Download the [dts file](https://github.com/wenzel-lab/open-microfluidics-workstation/blob/master/module-pi/pi_config/dt-blob.dts) and copy it into your Home folder.
* Install the Device Tree compiler by running `sudo apt install device-tree-compiler`
* Run the `dtc` command `sudo dtc -I dts -O dtb -o /boot/dt-blob.bin dt-blob.dts`

>i It is very useful to use the command `raspi-gpio get` to look at the setup of the GPIO pins to check that they are as you expect.

## Run the UI App {pagestep}

Download the [zip file](https://github.com/wenzel-lab/moldular-microfluidics-workstation-controller/blob/master/module-pi/webapp.zip), copy it, and extract the folder into your Home folder.

**Method 1:** Go to the web app folder and double click on `pi_webapp.py`. A programming editor will open the Python file, then run the code.

**Method 2:** Use the terminal window, then `cd webapp` and `python pi_webapp.py`

Use a browser and go to `https://0.0.0.0:5000` to use the Web App

## Run the UI App on startup {pagestep}

Once the folder and Python files are in your Home folder, configure the Raspberry Pi to run the web app on startup.

We must edit the `rc.local` file `sudo nano /etc/rc.local`

Add `sudo -H -u pi python3 /home/pi/webapp/pi_webapp.py &` before `exit 0` on the file

Then, save it with `CTL+O` > `Enter` > `CTL+X`, and reboot the system `sudo reboot`.

When the Raspberry Pi boot again, use a browser and go to `https://0.0.0.0:5000` to open the Web App.

>i **Note:** While the program is running in the background, you will not be able to use the camera. First, you must kill the process related to the program. To identify the process (number of PID), use `ps aux`. Then, use `sudo kill -9 PID` where `PID` is the process. If you want to run the program again, repeat **STEP 6** or reboot the system.

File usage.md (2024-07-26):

# Use your Stage

>i **Please Note:** This site is under construction.

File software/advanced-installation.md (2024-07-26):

# Advanced Installation

## Write your SD Card {pagestep}
You must install an operating system first to set up and use the Raspberry Pi board. Bullseye OS is a Debian-based computer operating system for Raspberry Pi board. Raspberry Pi OS 32-bit must be installed.

>i A pre-built SD card image is available. Go to [Simple Installation](software-installation.md) and follow the instructions. 

**Before you start, please make sure you have:**

* A computer with Internet
* A MicroSD card
* A SD card reader (OPTIONAL) 
* A SD card adapter (OPTIONAL)

**To write your MicroSD card:**

* Download the recommended .img file from [Raspberry Pi website](https://www.raspberrypi.com/software/operating-systems/) or install [Raspberry Pi imager](https://www.raspberrypi.com/software/) on your computer to access to an image.
* Use an adapter to connect your MicroSD card to your computer.
* Use a program such as [Etcher](https://www.balena.io/etcher) or [Raspberry Pi imager](https://www.raspberrypi.com/software/) to flash the .img file onto your MicroSD card.

More detailed information on installing a Raspberry Pi operating system image onto an SD card can be found [here on the Raspberry Pi website](https://www.raspberrypi.com/documentation/computers/getting-started.html#installing-the-operating-system).

**First boot:**

Connect your Pi to a display, mouse, keyboard, and power source. When the Pi first boots, you will be asked to complete a quick setup before rebooting.

Once you have installed and configured the Raspberry Pi OS, you can install the User Interface App.

## Enable SSH, SPI, VNC and Camera {pagestep}

**Method 1:** Use the graphical tool "Raspberry Pi Configuration". This is found under Menu > Preferences > Raspberry Pi Configuration. Then you must select the "Interfaces" tab and set SSH, SPI, VNC and Camera to "Enabled".

**Method 2:** From the command line or Terminal window, start by running `sudo raspi-config`. This will launch the raspi-config utility:

- Select “Interfacing Options”.
- Highlight the "SSH" option and activate **Select**.
- Select and activate **Yes**.
- Highlight and activate **Ok**.
- When prompted to reboot highlight and activate **Yes**.
- Repeat the previous steps to enable "SPI" and "Camera".

## Edit config.txt {pagestep}

We need to edit the config file `sudo nano /boot/config.txt`

Add `disable_camera_led=2` at the end of the file  

Then, save it with `CTL+O` > `Enter` > `CTL+X` and reboot the system `sudo reboot`.

## Plug in Camera {pagestep}

How to connect properly a Raspberry Pi camera and more information about the sensor can be found [here on the Raspberry Pi website](https://www.raspberrypi.com/documentation/accessories/camera.html). Use `vcgencmd get_camera` to verify if your camera was detected and `raspistill -o test.jpg` if it works.

>! Cameras are sensitive to static. Earth yourself before handling the PCB. A sink tap or similar should suffice if you don’t have an earthing strap.

## Install Libraries {pagestep}

The Python libraries that allow the Webb App to work on your Pi are the followings:

```
Flask 1.0.2
Flask-socketio 4.3.2
Werkzeug 0.14.1
Jinja2 2.10
Markupsafe 1.1.0
itsdangerous 0.24
eventlet 0.33.3
spidev 3.6
RPi.GPIO 0.7.1
picamera 1.13
Pillow 9.4.0
```
**Method 1:** Use the terminal window and install each of the above libraries with `pip install`. Example: `pip install Flask==1.0.2`

**Method 2:** Download [requirements.txt](https://github.com/wenzel-lab/open-microfluidics-workstation/blob/master/software/requirements.txt) file and copy it into your Home folder on your Pi. Use the terminal window and install all the libraries with `pip install -r requirements.txt` 

>i Use `pip list` to verify which modules are installed and their versions. 

## Set up the GPIO pin states {pagestep}

GPIO pins states must be modified during the bootup sequence to use them with the peripherals of the workstation. Our own custom `dt-blob.bin` file specifies which pin states should change:

* Download the [dts file](https://github.com/wenzel-lab/open-microfluidics-workstation/blob/master/module-pi/pi_config/dt-blob.dts) and copy it into your Home folder.
* Install the Device Tree compiler by running `sudo apt install device-tree-compiler`
* Run the `dtc` command `sudo dtc -I dts -O dtb -o /boot/dt-blob.bin dt-blob.dts`

>i It is very useful to use the command `raspi-gpio get` to look at the setup of the GPIO pins to check that they are as you expect.

## Run the UI App {pagestep}

Download the [zip file](), copy it, and extract the folder into your Home folder.

**Method 1:** Go to the web app folder and double click on `pi_webapp.py`. A programming editor will open the Python file, then run the code.

**Method 2:** Use the terminal window, then `cd webapp` and `python pi_webapp.py`

Use a browser and go to `https://0.0.0.0:5000` to use the Web App

## Run the UI App on startup {pagestep}

Once the folder and Python files are in your Home folder, configure the Raspberry Pi to run the web app on startup.

We must edit the `rc.local` file `sudo nano /etc/rc.local`

Add `sudo -H -u pi python3 /home/pi/webapp/pi_webapp.py &` before `exit 0` on the file

Then, save it with `CTL+O` > `Enter` > `CTL+X`, and reboot the system `sudo reboot`.

When the Raspberry Pi boot again, use a browser and go to `https://0.0.0.0:5000` to open the Web App.

>i **Note:** While the program is running in the background, you will not be able to use the camera. First, you must kill the process related to the program. To identify the process (number of PID), use `ps aux`. Then, use `sudo kill -9 PID` where `PID` is the process. If you want to run the program again, repeat **STEP 6** or reboot the system.

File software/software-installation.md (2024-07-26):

# Software Installation

The simplest way to set up the Raspberry Pi is to download the pre-built SD card image that contains a full operating system with all the necessary software pre-installed.

>i If you are familiar with command lines, go to [Advanced Installation](advanced-installation.md) and follow the instructions.

## Download SEMS OS {pagestep}

* Click [here](https://drive.google.com/file/d/1Vi45Qx171UzSz13v-zXnuIWUdMhgsN83/view?usp=sharing) to download the custom image. **Required:** Raspberry Pi 4 Model B (2GB RAM) or better.

## Write your SD Card {pagestep}

* Connect your MicroSD card to your computer. **Required:** a 8GB MicroSD card or better.
* Use a program such as [Etcher](https://www.balena.io/etcher) or [Raspberry Pi imager](https://www.raspberrypi.com/software/) to flash the .img file onto your MicroSD card.

More detailed information on installing a Raspberry Pi operating system image onto an SD card can be found [here on the Raspberry Pi website](https://www.raspberrypi.com/documentation/computers/getting-started.html#installing-the-operating-system).

## First boot and use {pagestep}

* Mount the microSD card with the OS on your Pi.
* Connect your Pi to a display, mouse, keyboard, and power source. When the Pi first boots, you could be asked to complete a quick setup or install updates.
* Click on the Desktop shortcut to start using the web app.

## Captured images {pagestep}

* Go to this directory `/home/pi/webapp/snapshots` to find and download the captured images.

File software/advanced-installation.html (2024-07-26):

# Strobe-enhanced microscopy stage

by Pierre Padilla-Huamantinco, Matías Hurtado-Labarca, and Tobias Wenzel

Latin American Hub for Bioimaging Through Open Hardware (LIBRE hub)

# Advanced Installation

## Step 1: Write your SD Card

You must install an operating system first to set up and use the Raspberry Pi board. Bullseye OS is a Debian-based computer operating system for Raspberry Pi board. Raspberry Pi OS 32-bit must be installed.

A pre-built SD card image is available. Go to Simple Installation and follow the instructions.

Before you start, please make sure you have:

- A computer with Internet
- A MicroSD card
- A SD card reader (OPTIONAL)
- A SD card adapter (OPTIONAL)

To write your MicroSD card:

- Download the recommended .img file from Raspberry Pi website (https://www.raspberrypi.com/software/operating-systems/) or install Raspberry Pi imager (https://www.raspberrypi.com/software/) on your computer to access to an image.
- Use an adapter to connect your MicroSD card to your computer.
- Use a program such as Etcher (https://www.balena.io/etcher) or Raspberry Pi imager (https://www.raspberrypi.com/software/) to flash the .img file onto your MicroSD card.

More detailed information on installing a Raspberry Pi operating system image onto an SD card can be found here on the Raspberry Pi website (https://www.raspberrypi.com/documentation/computers/getting-started.html).

First boot:

Connect your Pi to a display, mouse, keyboard, and power source. When the Pi first boots, you will be asked to complete a quick setup before rebooting.

Once you have installed and configured the Raspberry Pi OS, you can install the User Interface App.

## Step 2: Enable SSH, SPI, VNC and Camera

Method 1: Use the graphical tool "Raspberry Pi Configuration". This is found under Menu > Preferences > Raspberry Pi Configuration. Then you must select the "Interfaces" tab and set SSH, SPI, VNC and Camera to "Enabled".

Method 2: From the command line or Terminal window, start by running sudo raspi-config. This will launch the raspi-config utility:

- Select “Interfacing Options”.
- Highlight the "SSH" option and activate Select.
- Select and activate Yes.
- Highlight and activate Ok.
- When prompted to reboot highlight and activate Yes.
- Repeat the previous steps to enable "SPI" and "Camera".

## Step 3: Edit config.txt

We need to edit the config file sudo nano /boot/config.txt

Add disable_camera_led=2 at the end of the file

Then, save it with CTL+O > Enter > CTL+X and reboot the system sudo reboot.

## Step 4: Plug in Camera

How to connect properly a Raspberry Pi camera and more information about the sensor can be found here on the Raspberry Pi website (https://www.raspberrypi.com/documentation/accessories/camera.html). Use vcgencmd get_camera to verify if your camera was detected and raspistill -o test.jpg if it works.

Cameras are sensitive to static. Earth yourself before handling the PCB. A sink tap or similar should suffice if you don’t have an earthing strap.

## Step 5: Install Libraries

The Python libraries that allow the Webb App to work on your Pi are the followings:

Flask 1.0.2
Flask-socketio 4.3.2
Werkzeug 0.14.1
Jinja2 2.10
Markupsafe 1.1.0
itsdangerous 0.24
eventlet 0.33.3
spidev 3.6
RPi.GPIO 0.7.1
picamera 1.13
Pillow 9.4.0

Method 1: Use the terminal window and install each of the above libraries with pip install. Example: pip install Flask==1.0.2

Method 2: Download requirements.txt (https://github.com/wenzel-lab/open-microfluidics-workstation/blob/master/software/requirements.txt) file and copy it into your Home folder on your Pi. Use the terminal window and install all the libraries with pip install -r requirements.txt

Use pip list to verify which modules are installed and their versions.

## Step 6: Set up the GPIO pin states

GPIO pins states must be modified during the bootup sequence to use them with the peripherals of the workstation. Our own custom dt-blob.bin file specifies which pin states should change:

- Download the dts file (https://github.com/wenzel-lab/open-microfluidics-workstation/blob/master/module-pi/pi_config/dt-blob.dts) and copy it into your Home folder.
- Install the Device Tree compiler by running sudo apt install device-tree-compiler
- Run the dtc command sudo dtc -I dts -O dtb -o /boot/dt-blob.bin dt-blob.dts

It is very useful to use the command raspi-gpio get to look at the setup of the GPIO pins to check that they are as you expect.

## Step 7: Run the UI App

Download the zip file, copy it, and extract the folder into your Home folder.

Method 1: Go to the web app folder and double click on pi_webapp.py. A programming editor will open the Python file, then run the code.

Method 2: Use the terminal window, then cd webapp and python pi_webapp.py

Use a browser and go to https://0.0.0.0:5000 to use the Web App

## Step 8: Run the UI App on startup

Once the folder and Python files are in your Home folder, configure the Raspberry Pi to run the web app on startup.

We must edit the rc.local file sudo nano /etc/rc.local

Add sudo -H -u pi python3 /home/pi/webapp/pi_webapp.py & before exit 0 on the file

Then, save it with CTL+O > Enter > CTL+X, and reboot the system sudo reboot.

When the Raspberry Pi boot again, use a browser and go to https://0.0.0.0:5000 to open the Web App.

Note: While the program is running in the background, you will not be able to use the camera. First, you must kill the process related to the program. To identify the process (number of PID), use ps aux. Then, use sudo kill -9 PID where PID is the process. If you want to run the program again, repeat STEP 6 or reboot the system.

GitBuilding logo Documentation powered by GitBuilding (https://gitbuilding.io)

©2024 Pierre Padilla-Huamantinco, Matías Hurtado-Labarca, and Tobias Wenzel

Contact: librehub@uc.cl

Strobe-enhanced microscopy stage is released under CERN-OHL-S-2.0.

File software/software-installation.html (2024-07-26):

# Strobe-enhanced microscopy stage

by Pierre Padilla-Huamantinco, Matías Hurtado-Labarca, and Tobias Wenzel

Latin American Hub for Bioimaging Through Open Hardware (LIBRE hub)

# Software Installation

The simplest way to set up the Raspberry Pi is to download the pre-built SD card image that contains a full operating system with all the necessary software pre-installed.

If you are familiar with command lines, go to Advanced Installation and follow the instructions.

## Step 1: Download SEMS OS

- Click here (https://drive.google.com/file/d/1Vi45Qx171UzSz13v-zXnuIWUdMhgsN83/view?usp=sharing) to download the custom image. Required: Raspberry Pi 4 Model B (2GB RAM) or better.

## Step 2: Write your SD Card

- Connect your MicroSD card to your computer. Required: a 8GB MicroSD card or better.
- Use a program such as Etcher (https://www.balena.io/etcher) or Raspberry Pi imager (https://www.raspberrypi.com/software/) to flash the .img file onto your MicroSD card.

More detailed information on installing a Raspberry Pi operating system image onto an SD card can be found here on the Raspberry Pi website (https://www.raspberrypi.com/documentation/computers/getting-started.html).

## Step 3: First boot and use

- Mount the microSD card with the OS on your Pi.
- Connect your Pi to a display, mouse, keyboard, and power source. When the Pi first boots, you could be asked to complete a quick setup or install updates.
- Click on the Desktop shortcut to start using the web app.

## Step 4: Captured images

- Go to this directory /home/pi/webapp/snapshots to find and download the captured images.

GitBuilding logo Documentation powered by GitBuilding (https://gitbuilding.io)

©2024 Pierre Padilla-Huamantinco, Matías Hurtado-Labarca, and Tobias Wenzel

Contact: librehub@uc.cl

Strobe-enhanced microscopy stage is released under CERN-OHL-S-2.0.

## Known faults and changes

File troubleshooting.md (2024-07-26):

# Troubleshooting

>i **Please Note:** This site is under construction.

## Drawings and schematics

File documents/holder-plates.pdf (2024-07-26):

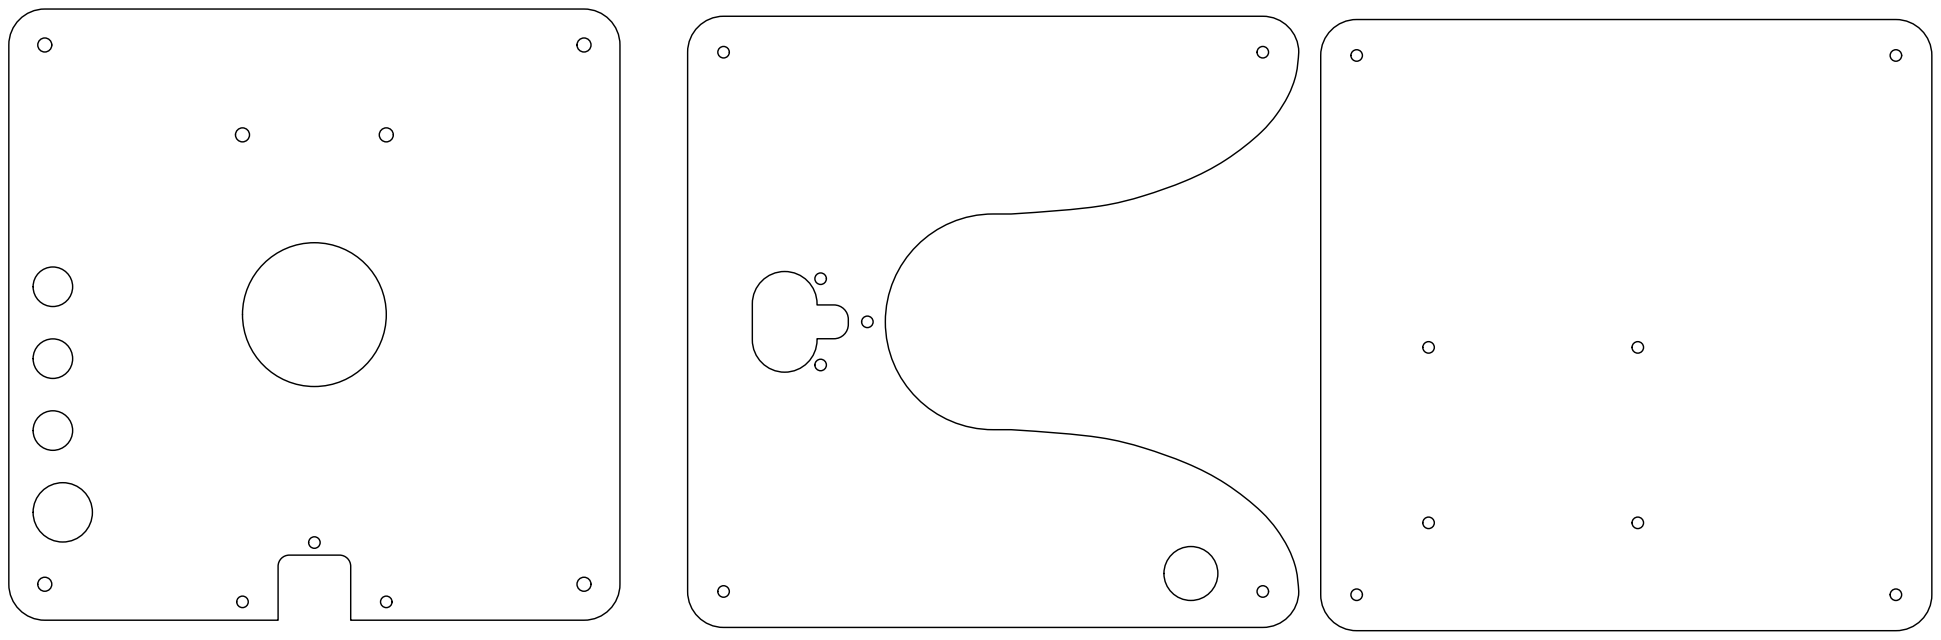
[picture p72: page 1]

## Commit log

2023-05-23 Deploying to main from @ b8258ef7d03a3a83451d9e2eb6dc50b1b73e1941 🚀
    [index_BOM.csv]
2023-05-23 Deploying to main from @ faf954b493e1a7d1cb32da031e6e599126f50ef6 🚀
2023-05-23 Deploying to main from @ 90412c5417b891d5e61c8f5a5a8985592f0f62f0 🚀
2023-05-23 Deploying to main from @ 2c414f49b8ac218702784c85f67b7a6f69e34016 🚀
2023-06-07 Deploying to main from @ 028bc8ead0f71d2fdf1d4c5206ff56b6d56bf444 🚀
    [index_BOM.csv]
2023-07-11 Documentation v1
    [actuator-assembly-tools.stl, arm-pin.stl, bottom-plate.dxf, bottom-plate.stl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]
2023-07-11 Deploying to main from @ 77fb46ab9104f08c6a745814efdbd876ed381785 🚀
    [3-level-station_BOM.csv]
2023-07-12 Deploying to main from @ bd62b02ade24eebb3eb9b94933db662d6e4100c0 🚀
2023-07-13 Deploying to main from @ bef728c6e4fff6ebd33139ff8572be7986f7fd7e 🚀
    [3-level-station_BOM.csv]
2023-07-13 Deploying to main from @ 5e696a8e9309f028cc2e9572ecde6702165a7d4f 🚀
2023-07-21 Deploying to main from @ 9107b05ac7c8bb2d0aa77989e5a0394d7a76e8e1 🚀
2023-07-25 Deploying to main from @ 6c54a7b342cf36e458b24d136807506a697a28f1 🚀
2023-07-25 Deploying to main from @ b65b7ed4011e47748e738d26c86293fadbc0e8cb 🚀
2023-07-31 Deploying to main from @ 49948fa58721ed4a3004a468869bebffdbaa3efb 🚀
2023-08-07 Deploying to main from @ 75deeacb7fd9e9970a35f3a134b92e4da5bafefc 🚀
    [actuator-assembly-tools.stl, bottom-plate.dxf, leg_test.stl, middle-plate.dxf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]
2023-08-07 Deploying to main from @ 234c4d7713559114b1ca338c6e06b64da3d895fb 🚀
    [0.2ml-double.stl, 0.6ml-double.stl, 1.5ml-single.stl, 3-level-station_BOM.csv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]
2023-08-07 Deploying to main from @ 94e5ee5d860ec2f81822dd5ae065016e7f5e708d 🚀
    [3-level-station_BOM.csv, top-plate.dxf]
2023-08-07 Deploying to main from @ 372647629e15e94db50caaf3749baaae4fd96f40 🚀
2023-08-07 Deploying to main from @ d81fd005051325fe6195259b602e63de2882803c 🚀
2023-08-07 Deploying to main from @ 1d14ee66e9c59865c4109d68046f3b547a865f1c 🚀
    [3-level-station_BOM.csv]
2023-08-07 Revert "Deploying to main from @ 1d14ee66e9c59865c4109d68046f3b547a865f1c 🚀"
    This reverts commit 18a7cbf5ee8970da4c17eec2b1ae71ce5d6cab59.
    [3-level-station_BOM.csv]
2023-08-07 Revert "Delete Variations directory"
    This reverts commit 1d14ee66e9c59865c4109d68046f3b547a865f1c.
    [0.2ml-double.stl, 0.6ml-double.stl, 1.5ml-single.stl, 3D-Bottom-plate.stl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]
2023-08-07 Revert "Deploying to main from @ d81fd005051325fe6195259b602e63de2882803c 🚀"
    This reverts commit 1a5c98a0ce5d1add60ab640f8e308523b94bc725.
2023-08-07 Revert "Deploying to main from @ 94e5ee5d860ec2f81822dd5ae065016e7f5e708d 🚀"
    This reverts commit a3d98f320cc2f3f4ca66de4e8f255f6f0af53f5b.
    [3-level-station_BOM.csv, top-plate.dxf]
2023-08-07 Revert "Deploying to main from @ 372647629e15e94db50caaf3749baaae4fd96f40 🚀"
    This reverts commit 5da0da73448e9658edd3e8464632511a1948792e.
2023-08-07 Revert "Deploying to main from @ 234c4d7713559114b1ca338c6e06b64da3d895fb 🚀"
    This reverts commit 66a00159f4ba1e3f056d37041c594a746e5ebd91.
    [0.2ml-double.stl, 0.6ml-double.stl, 1.5ml-single.stl, 3-level-station_BOM.csv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]
2023-08-07 Revert "Deploying to main from @ 75deeacb7fd9e9970a35f3a134b92e4da5bafefc 🚀"
    This reverts commit fb6ad3b5075f8048b974a019e855e72edaf93390.
    [actuator-assembly-tools.stl, bottom-plate.dxf, leg_test.stl, middle-plate.dxf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]
2023-08-07 Deploying to main from @ 31919bbaa31400f5afdc078f1839f02b19c3d7b2 🚀
    [3-level-station_BOM.csv]
2023-08-10 Deploying to main from @ 0984d1786512db2f8a496fec988d82a35f65460d 🚀
    [0.2ml-double.stl, 0.6ml-double.stl, 1.5ml-single.stl, 3D-Bottom-plate.stl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]
2023-09-22 Deploying to main from @ d82559e600e3162e837722cafa4e30a3cdb50a57 🚀
2023-11-29 Deploying to main from @ 1fd92090aa83f79a3a4975d805bb712370cc03f1 🚀
    [LensSpacer.stl, armpin.stl, basefocusing.stl, cameraholder.stl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]
2023-11-29 Update building documentation
    [0.2ml-double.stl, 0.6ml-double.stl, 1.5ml-single.stl, 15ml-single.stl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]
2023-11-29 Deploying to main from @ 175ef7e6bb87f073cb70f9375124ce6db9259c6f 🚀
    [3-level-station_BOM.csv]
2023-11-29 Deploying to main from @ 869058e14a7f2d5a5ab1e06fd1094242d6935bb9 🚀
2024-07-26 Deploying to main from @ 19423d02cb1fef5e4d7397a9c9a075dbae8b73ad 🚀
2024-07-29 Deploying to main from @ 418587e46152454619cf2b66904c32f0e3b0cf17 🚀
    [3-level-station_BOM.csv]
